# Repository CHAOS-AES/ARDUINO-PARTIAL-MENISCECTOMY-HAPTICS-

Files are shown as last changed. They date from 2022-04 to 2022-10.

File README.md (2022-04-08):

# PARTIAL MENISCECTOMY HAPTICS

This is a repository for a project on reality-based modelling of partial meniscectomy.

This project builds on other open-source projects:
- Arduino SimpleFOC library for BLDC control, MIT Licence (Copyright (c) Antun Skuric).
- Basic Linear Algebra library for Arduino, MIT Licence (Copyright (c) tomstewart89).

Repository contains code and CAD models for:
1) Prototype for collecting force-position data from Acufect Upbiter Punch, with ARDUINO MKR Zero based FSR-sensor and potentiometer.
2) Protype for rendering haptic feedback of partial meniscectomy using self-designed hardware, Arduino DUE with SimpleFOC shield, BLDC motor, and AMT 102V encoder.
3) Arduino code for sensor fusion of real-time finite element simulation and empirical data using Kalman Filter.
4) Visualization of partial meniscectomy punch using Processing.

Prototype for collecting data:


Prototype for haptic rendering:




Instructions for running haptic rendering:
1) Build hardware according to bill-of-materials and CAD-models.
2) Download Arduino code.
3) Install hapticFEM-library, simpleFOC-library, Basic Linear Algebra library.
4) Run Arduino sketch: KF_HapticEstimate_with_FEMlib.ino
5) Launch "Processing" and run "PUNCHER_3D_RevF.pde".

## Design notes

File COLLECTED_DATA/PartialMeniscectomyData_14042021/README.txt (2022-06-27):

This folder contains experimental data from a tool-tissue interaction data collection experiment using an Acufex Upbiter Punch. The data was collected from a cadaveric meniscus.

Folders:
PART I: Samples with tape covering FSR sensor. Idea was to get better force distribution over FSR, but ended up biasing measures (force not being zero unloaded).
PART II: Tape was removed. Zero force on zero load, but pay attention to force behavior.

The dataset consists of five columns:
1) fsrReading - this is the raw reading of the force sensitive resistor.
2) fsrForce - this is the fsr-force converted to Newtons from a calibration function.
3) potVal - this is the raw potentiometer reading.
3) anglePres - this is the potentiometer reading converted to degrees.
4) currentMillis - this is the time stamp in milliseconds.

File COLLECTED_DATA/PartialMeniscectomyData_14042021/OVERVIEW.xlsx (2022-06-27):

 | Tissue Cutting test 14042021
 | Each test includes a series of at least 10 cuts.
Test # | Tests performed | Comments | Time stamp
1 | Blank Slow | Blank cut in sheet of print paper. Tape mounted over FSR to distribute pressure. | 1758
2 | Blank Fast | Blank cut in sheet of print paper. Tape mounted over FSR to distribute pressure. | 1759
3 | Meniscus Slow | Slow and controlled cut in meniscus. Tape mounted over FSR to distribute pressure. | 1804
4 | Meniscus Slow | Slow and controlled cut in meniscus. Tape mounted over FSR to distribute pressure. | 1811
5 | Meniscus Fast | Faster meniscus cut. Tape mounted over FSR to distribute pressure. | 1807
6 | Meniscus Fast | Faster meniscus cut. Tape mounted over FSR to distribute pressure. | 1814
7 | Blank Slow | Blank cut in sheet of print paper. Tape removed. | 1819
8 | Blank Fast | Blank cut in sheet of print paper. Tape removed. | 1821
9 | Meniscus Slow | Slow and controlled cut in meniscus. Tape removed. | 1824
10 | Meniscus Slow | Slow and controlled cut in meniscus. Tape removed. Meniscus removed from knee. | 1839
11 | Meniscus Fast | Faster meniscus cuts. Tape removed. | 1826
12 | Meniscus Fast | Faster meniscus cuts. Tape removed. Meniscus removed from knee. | 1842

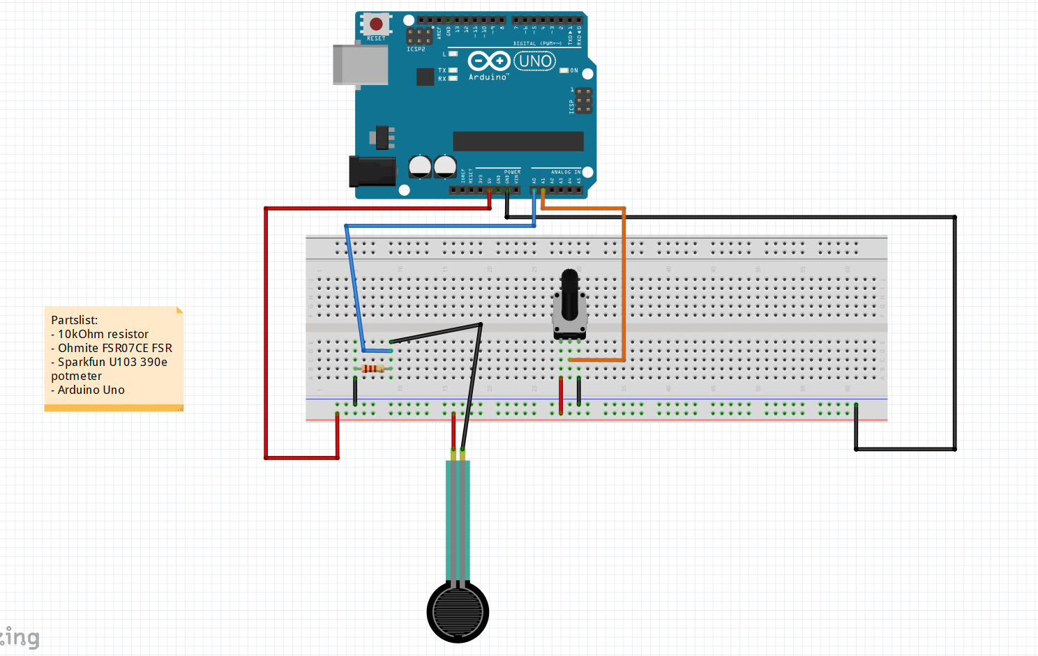
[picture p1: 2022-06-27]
DATA_COLLECTION/schematic.PNG

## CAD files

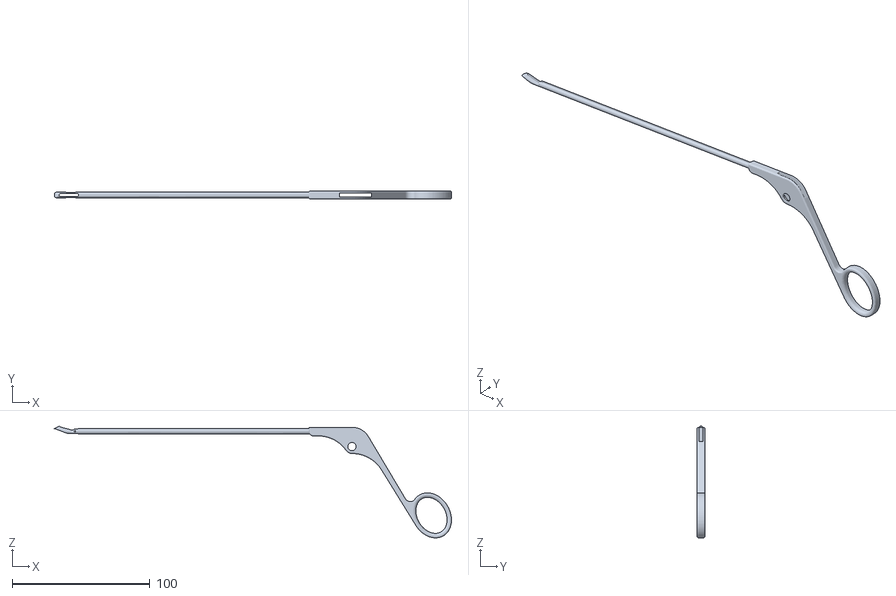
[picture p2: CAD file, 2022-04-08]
HAPTIC_RENDERING/PROCESSING(VISUALIZATION)/PUNCHER_3D_RevF/ACUFEX_PUNCH_MAIN_BODY.obj
287.8 x 5.74 x 81.0

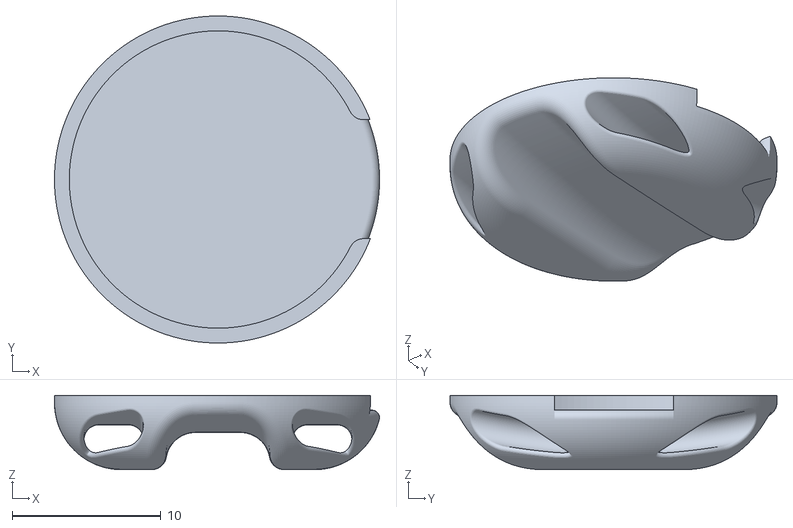
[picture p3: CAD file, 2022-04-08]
DATA_COLLECTION/CAD/3D-print/FSR07_thumb_adapter_RevB.stl
21.9 x 22.0 x 5.00

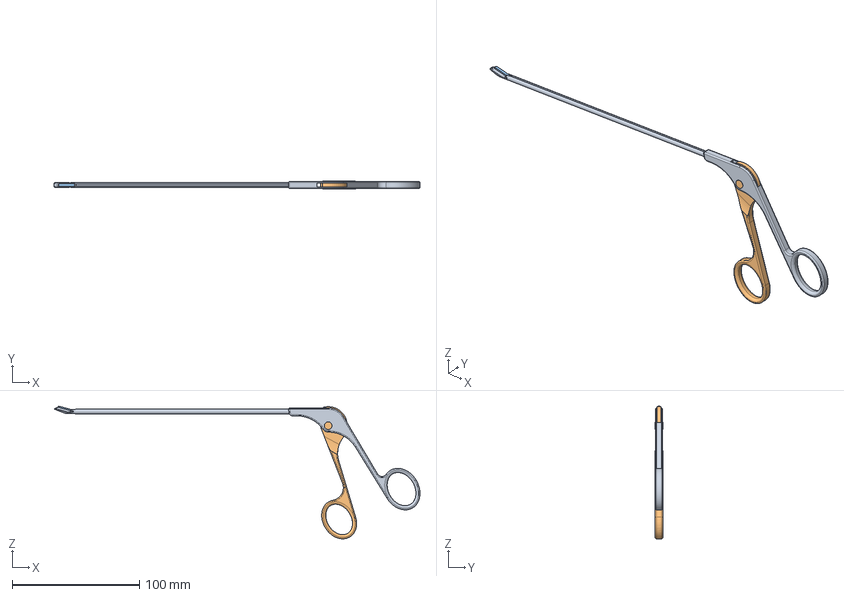
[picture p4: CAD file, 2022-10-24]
DATA_COLLECTION/CAD/STP/ACUFEX_1_5mm_UPBITER_PUNCH_7207735.stp
287.8 x 6.00 x 104.4 mm
ACUFEX_PUNCH_MAIN_BODY
trigger_CSYS_translate
ACUFEX_PUNCHER

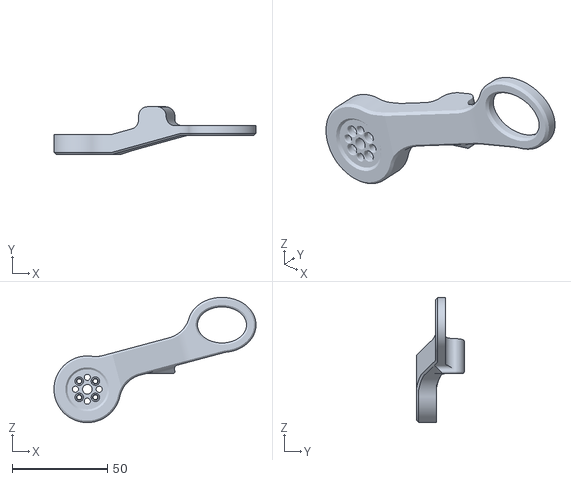
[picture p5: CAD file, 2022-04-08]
HAPTIC_RENDERING/CAD/3D-PRINT/FINGER_HANDLE_REVD.stl
106.1 x 25.0 x 65.7

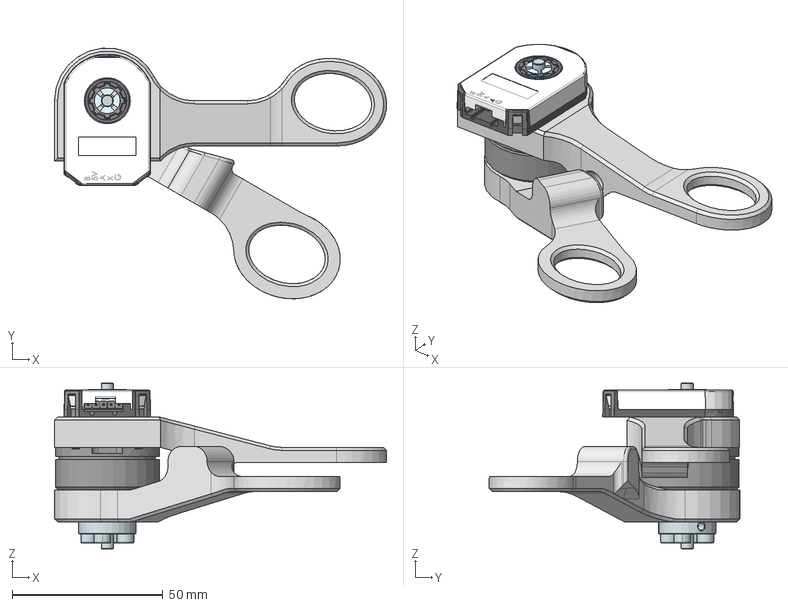
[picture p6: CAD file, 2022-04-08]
HAPTIC_RENDERING/CAD/STEP/FINGER_HAPTIC_DEVICE_REVD.stp
110.1 x 83.1 x 55.0 mm
GM2804_BLDC_motor
THUMB_HANDLE_REVD
FINGER_HANDLE_REVD
Transmitter-board AMT10_AMT-102__id6_x_t
Transmitter-board AMT10_AMT-102__id11_x_t
Transmitter-board AMT10_AMT-102__id16_x_t
Transmitter-board AMT10_AMT-102__id21_x_t
Transmitter-board AMT10_AMT-102__id26_x_t
Transmitter-board AMT10_AMT-102__id31_x_t
Transmitter-board AMT10_AMT-102__id36_x_t
Rotor-board-REV F_id41_x_t
Receiver-board_id46_x_t
AMT10X-Shaft-Adaptor-REV-E_id51_x_t
AMT-Hub-Bottom-REV-B_id56_x_t
AMT-Hub-Top-REV-D1_id61_x_t
AMT-Sleeve-REV-D_ 2 mm__id66_x_t
AMT-102-Top-Cover-REV-I_id71_x_t
AMT-102-Base-REV-K_id76_x_t
4mm_SHAFT
POLULU_4MM_SHAFT_CLAMP
BALL_BEARING_RS_612-5789
BOLT_DIN912_M2X10 x 4
BOLT_DIN912_M2_5X10 x 4
NUT_DIN934_M3 x 6
BOLT_DIN912_M3X12_ x 6
SET_SCREW_M3X6

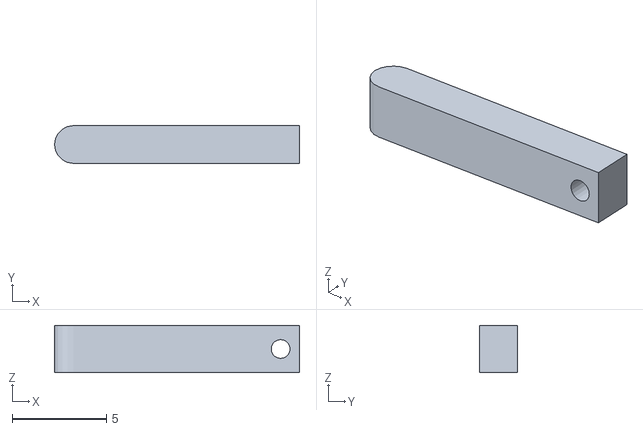
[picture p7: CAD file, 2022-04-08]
HAPTIC_RENDERING/PROCESSING(VISUALIZATION)/PUNCHER_3D_RevF/ACUFEX_PUNCHER.obj
13.0 x 2.00 x 2.50

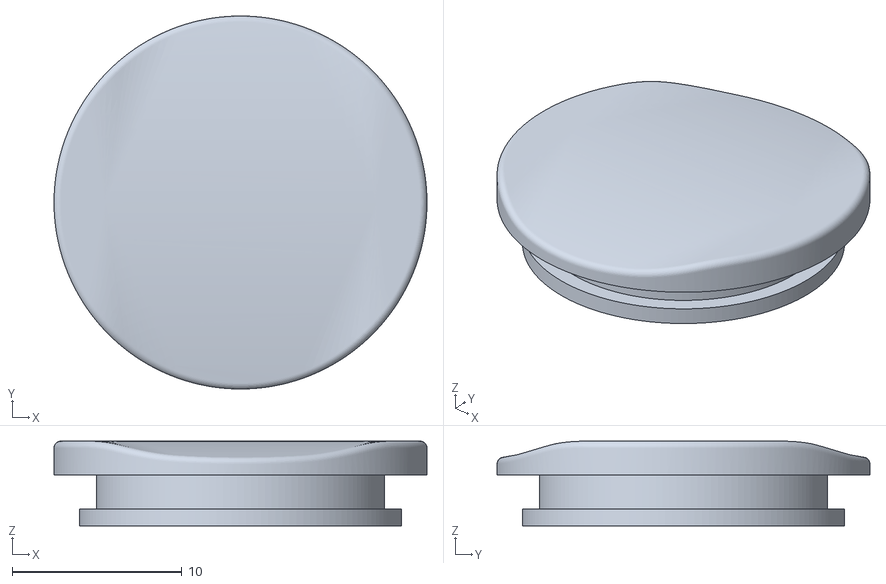
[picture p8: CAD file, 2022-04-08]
DATA_COLLECTION/CAD/3D-print/FSR_TOP.stl
22.0 x 22.0 x 5.00

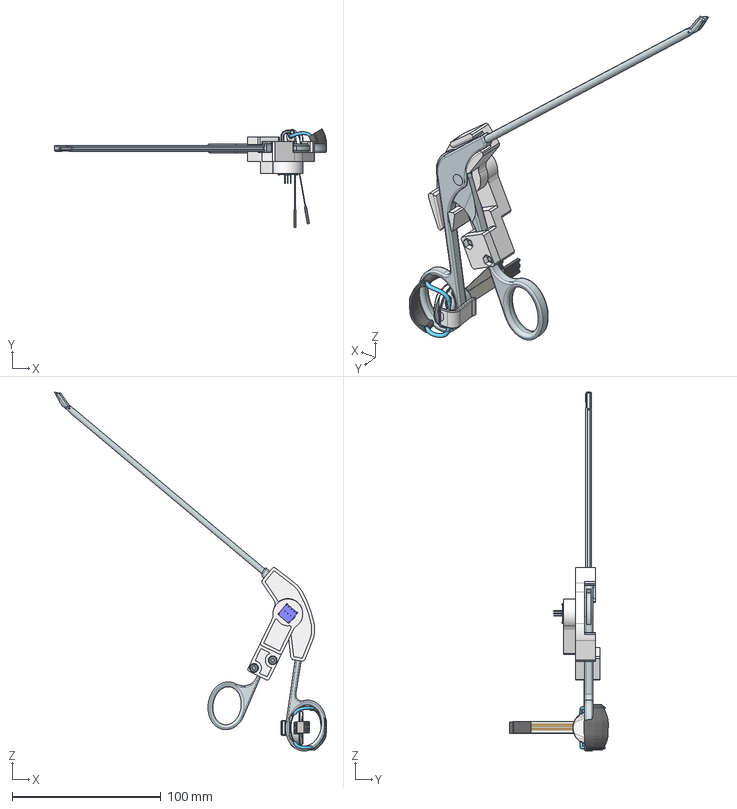
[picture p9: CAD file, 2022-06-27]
DATA_COLLECTION/CAD/STP/Acufex_Puncher_Setup.stp
182.8 x 66.2 x 240.9 mm
FSR07CE x 2
FSR07_thumb_adapter
FSR07_THUMB_ADAPTER_TOP
Rope_attachment
Strap
hand_import
ACUFEX_PUNCH_MAIN_BODY
trigger_CSYS_translate
ACUFEX_PUNCHER
COM-09806_Potentiometer x 2
POTMETER_FRAME_1
POTMETER_FRAME_2
bolt_din912_m3x12 x 2
POTMETER_FRAME_3
FSR_BASE
FSR_TOP

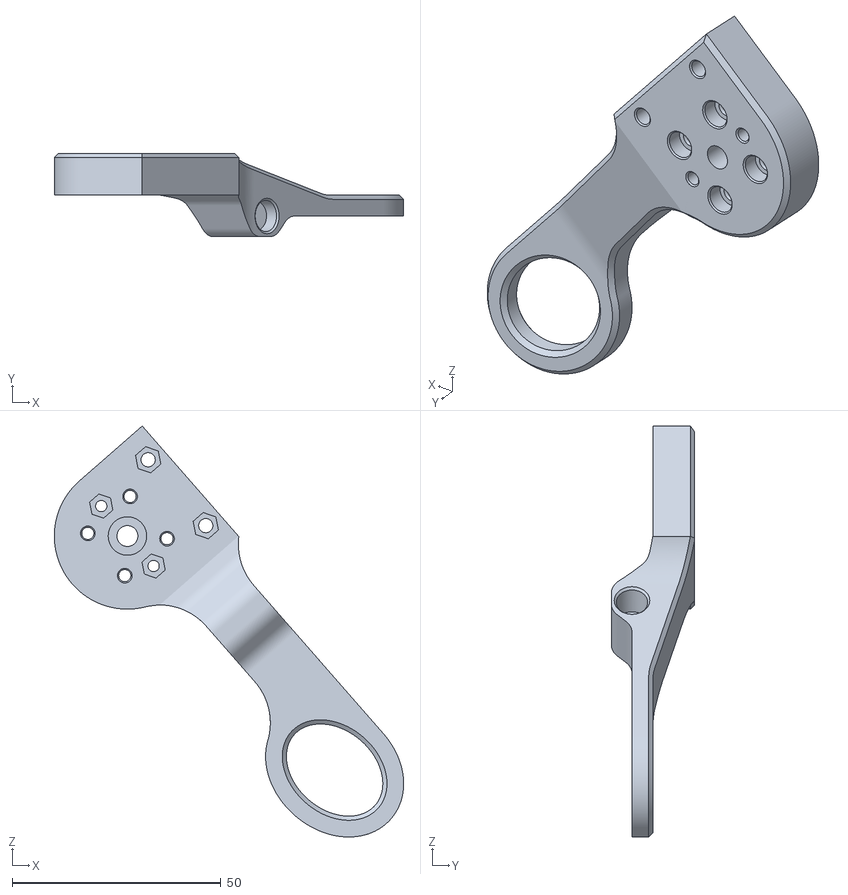
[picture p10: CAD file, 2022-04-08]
HAPTIC_RENDERING/CAD/3D-PRINT/THUMB_HANDLE_REVD.stl
83.6 x 19.9 x 98.4

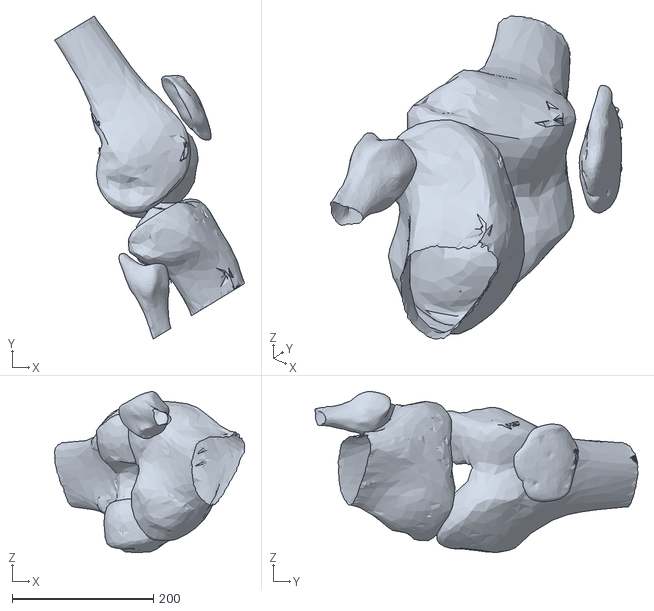
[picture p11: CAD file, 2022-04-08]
HAPTIC_RENDERING/PROCESSING(VISUALIZATION)/PUNCHER_3D_RevF/bone_medullar.obj
269.1 x 457.2 x 228.0

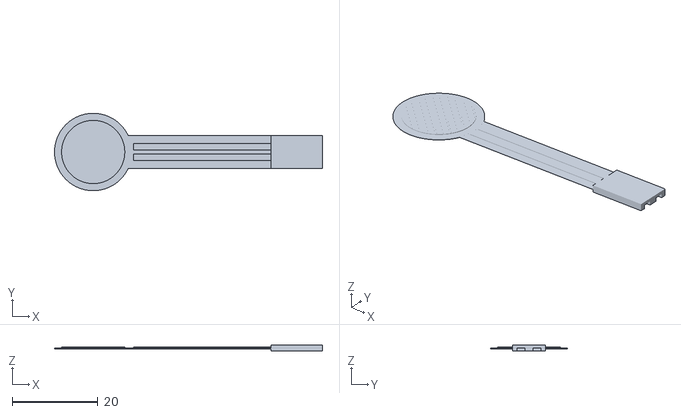
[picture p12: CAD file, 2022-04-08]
DATA_COLLECTION/CAD/3D-print/FSR07CE.stl
62.3 x 18.0 x 1.50

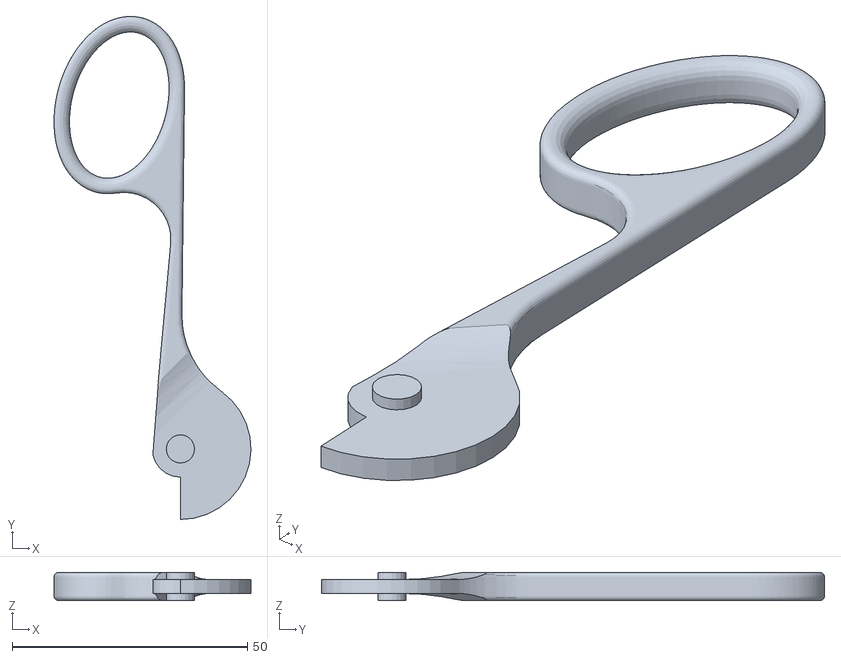
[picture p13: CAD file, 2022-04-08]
HAPTIC_RENDERING/PROCESSING(VISUALIZATION)/PUNCHER_3D_RevF/TRIGGER_NEW_CSYS.obj
41.9 x 106.9 x 6.00

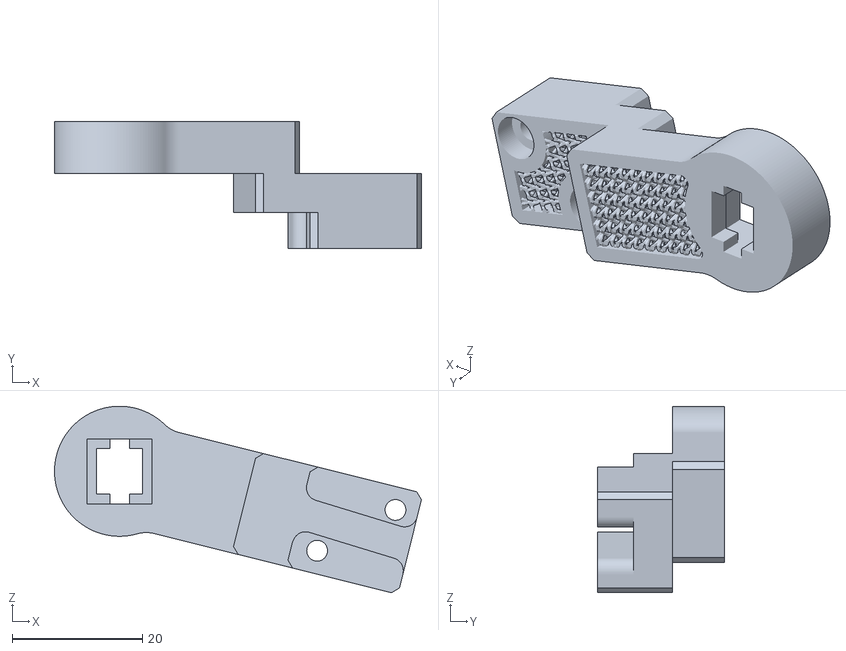
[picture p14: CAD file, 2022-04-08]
DATA_COLLECTION/CAD/3D-print/POTMETER_FRAME_2_RevC.stl
56.4 x 19.5 x 28.7

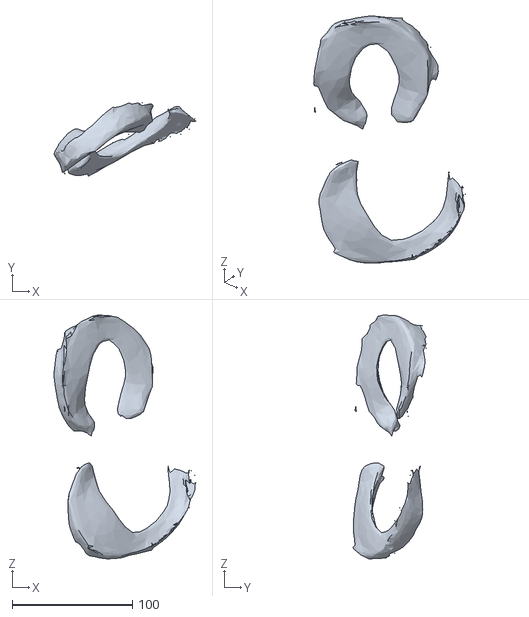
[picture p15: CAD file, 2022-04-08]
HAPTIC_RENDERING/PROCESSING(VISUALIZATION)/PUNCHER_3D_RevF/meniscus.obj
118.1 x 61.4 x 203.2

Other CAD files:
DATA_COLLECTION/CAD/3D-print/FSR_BASE_RevA.stl
HAPTIC_RENDERING/PROCESSING(VISUALIZATION)/PUNCHER_3D_RevF/ACUFEX_TRIGGER.obj
DATA_COLLECTION/CAD/3D-print/FSR07_THUMB_ADAPTER_TOP_RevB.stl
HAPTIC_RENDERING/PROCESSING(VISUALIZATION)/PUNCHER_3D_RevF/fibula.obj
DATA_COLLECTION/CAD/3D-print/POTMETER_FRAME_1_RevC.stl
DATA_COLLECTION/CAD/3D-print/POTMETER_FRAME_3.stl
HAPTIC_RENDERING/PROCESSING(VISUALIZATION)/PUNCHER_3D_RevF/MENISCUS_BUCKET_HANDLE.obj
HAPTIC_RENDERING/PROCESSING(VISUALIZATION)/PUNCHER_3D_RevF/PUNCHER_OBJ.obj
HAPTIC_RENDERING/PROCESSING(VISUALIZATION)/PUNCHER_3D_RevF/tibia.obj

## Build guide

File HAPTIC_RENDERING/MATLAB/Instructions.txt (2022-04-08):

Matlab script for tuning kalman filter parameters Q and R.

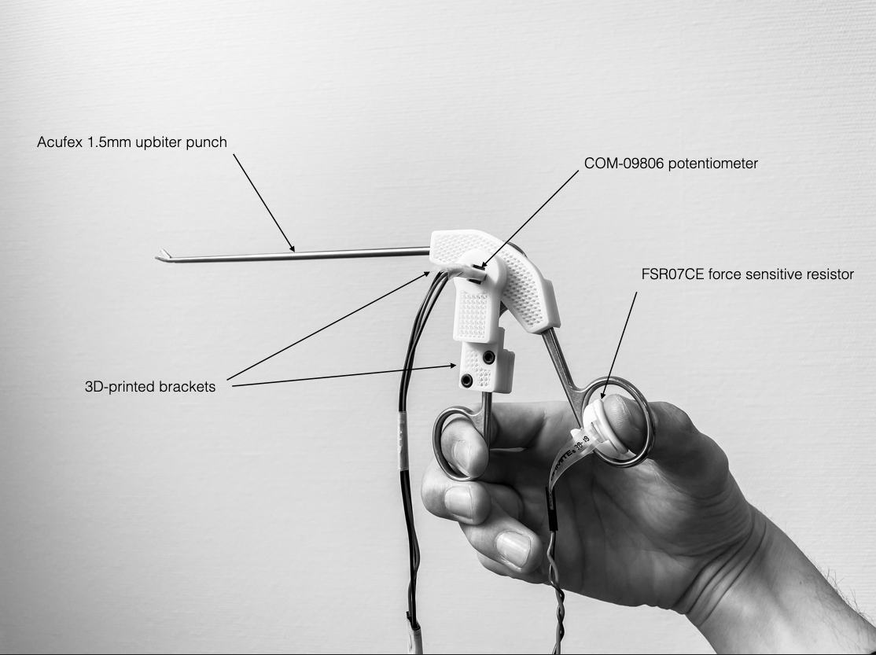
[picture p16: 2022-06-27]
DATA_COLLECTION/setup.PNG

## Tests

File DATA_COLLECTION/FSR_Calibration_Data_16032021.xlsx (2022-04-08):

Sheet: Curve Fitting
FSR Reading | Weight reading (g)
0 | 0 |  | Acceptable readings from 200g to 900g
170 | 60
260 | 250
410 | 300
600 | 350
700 | 400
760 | 450
710 | 500
0 | 0
150 | 130
200 | 200
300 | 250
420 | 300
530 | 400
650 | 500
770 | 600
950 | 700
970 | 800
960 | 900
900 | 1000
1000 | 1100
1023 | 1200
0 | 0
300 | 100
200 | 150
250 | 200
500 | 300
550 | 400
600 | 500
650 | 600
870 | 700
880 | 800
950 | 900
890 | 1000
980 | 1100
950 | 1200
900 | 1300 | Weigh reading (g) | FSR1 | FSR2 | FSR3
 |  | 130 | 150 | 200 | 150
 |  | 200 | 200 | 250 | 200
 |  | 300 | 420 | 500 | 500
0 | 0 | 400 | 530 | 550 | 590
150 | 110 | 500 | 650 | 600 | 670
200 | 200 | 600 | 770 | 650 | 800
500 | 300 | 700 | 950 | 870 | 750
590 | 400 | 800 | 970 | 880 | 850
670 | 500 | 900 | 960 | 950 | 1000
800 | 600
750 | 700
850 | 800
1000 | 900
930 | 1000
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

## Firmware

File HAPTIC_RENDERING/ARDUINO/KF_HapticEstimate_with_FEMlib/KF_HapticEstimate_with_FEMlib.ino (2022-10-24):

/**

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
 
 PROJECT DESCRIPTION: Real time finite-element based haptic rendering with Kalman Filter estimation of force from empirical data. Interfacing with ARDUINO DUE microcontroller, BGM2804 BLDC Motor, CUI AMT 102V Encoder.
 Based on SimpleFOC library for BLDC control (Copyright (c) 2020 Antun Skuric) 
 Finite Element implementation based on MATLAB code by Morten D. Pedersen, NTNU

  */
  
//*************************************************************************************
//DECLARE DEPENDENCIES START***********************************************************
 
#include <SimpleFOC.h> // FOR CONTROLLING BLDC Motor: https://github.com/simplefoc/Arduino-FOC
#include <hapticFEM.hpp>
#include <BasicLinearAlgebra.h> // FOR MATRIX OPERATIONS: https://github.com/tomstewart89/BasicLinearAlgebra 
#include <ElementStorage.h> // For BLA library

//using namespace BLA; //Using namespace basic linear algebra

//DECLARE DEPENDENCIES END************************************************************
//*************************************************************************************


//*************************************************************************************
//INITIALIZATION START*****************************************************************

  #define DOF 5 // Defines number of elements in rubber band model
  

  //Define Kalman Filter matrices
  BLA::Matrix<2,2> Q = {7.0275, 0.02772, 0.2772, 6.1024}; //System covariance matrix
  BLA::Matrix<1> R_FEM = {0.001}; // Measurement variance from FEM
  BLA::Matrix<1> R_empirical = {7.742}; // Measurement variance from empirical measurements
  //BLA::Matrix<1> R_empirical = {0.7742}; // Measurement variance from empirical measurements
  //BLA::Matrix<1> R_empirical = {77.42}; // Measurement variance from empirical measurements
  BLA::Matrix<1> R = R_FEM;

  BLA::Matrix<2,2> A = {1, 1, 0, 1}; //System matrix
  BLA::Matrix<2,2> Ad = A;
  BLA::Matrix<2,1> B = {1, 0};       //Input matrix
  BLA::Matrix<2,1> Bd = B;
  BLA::Matrix<1,2> H = {1, 0};       //Measurement matrix
  BLA::Matrix<2,1> HTransposed = ~H; //Measurement matrix transposed
  BLA::Matrix<1> u = {0};            //Input     
  BLA::Matrix<2,2> Id = {1, 0, 0, 1};//Identity matrix  

  BLA::Matrix<1> forceMeasurement = {0};
  double FEMforceMeasurement = 0;
  float maxFemForce = 0;
  float yieldForce = 7; // [N] Max FEM yield force
  float dTheta = 0;
  float xhDegPreviousStep = 0;
  float forceMovingAvg = 0;
  float forceMovingAvgLast = 0;
  float forceMovingAvgLastLast = 0;
  BLA::Matrix<2,2> Pplus = {0, 0, 0, 0};
  BLA::Matrix<2,1> xhat = {0, 0}; // Initial conditions. Zero force, zero stiffness.
  
  


//*************************************************************************************
//FUNCTION PERFORMING EMPIRICAL FORCE CALCULATION START********************************

BLA::Matrix<1> empiricalData(float xhDeg){
  //This function takes in a position value [deg] and returns a force signal [N]

  //BLA::Matrix<1> empForceMeasurement;
  double empForceMeasurement;
  double theta = (xhDeg - 16)/2; //Offset and scaling of theta range to fit FEM. Remove if not needed.
  
  // <row, column>
  BLA::Matrix<76,1> empForce;
  empForce = {0.000,0.000,0.000,0.008,0.008,0.000,0.000,0.000,0.000,0.008,0.008,0.008,0.008,0.008,0.008,0.008,0.000,0.084,0.228,0.823,1.006,1.789,2.217,2.791,3.313,3.798,4.096,4.187,4.220,4.302,4.344,4.220,4.327,4.236,4.369,4.253,4.277,4.277,4.145,4.072,3.894,3.894,3.999,4.154,3.966,4.015,3.798,3.726,3.750,3.774,3.814,3.679,3.806,3.894,3.950,4.056,4.039,3.983,4.007,3.910,3.894,3.886,4.015,4.031,3.958,3.950,4.031,4.007,4.064,4.015,4.113,4.031,3.983,4.056,4.080,4.344};
  
  BLA::Matrix<76,1> empTheta;
  empTheta = {2.079,2.188,2.300,2.414,2.526,2.636,2.742,2.842,2.939,3.033,3.127,3.222,3.322,3.430,3.547,3.675,3.813,3.961,4.118,4.283,4.453,4.629,4.807,4.988,5.171,5.357,5.545,5.737,5.932,6.132,6.335,6.542,6.752,6.966,7.183,7.404,7.627,7.854,8.083,8.315,8.546,8.777,9.003,9.221,9.429,9.621,9.796,9.950,10.082,10.192,10.280,10.349,10.400,10.438,10.465,10.485,10.500,10.514,10.528,10.543,10.559,10.576,10.595,10.615,10.635,10.656,10.675,10.694,10.712,10.729,10.745,10.761,10.776,10.791,10.806,10.820};

  // Linear interpolation

  for (int i = 0; i<75; i++){
      if ((theta > empTheta(i)) && (theta <= empTheta(i+1))){
          empForceMeasurement = empForce(i) + ((empForce(i+1) - empForce(i))*((theta - empTheta(i))/(empTheta(i+1) - empTheta(i))));
      } 
  }

    if (empForceMeasurement > 4.29){
    empForceMeasurement = 4.29;
  } else if (empForceMeasurement < 0.01){
    empForceMeasurement = 0.01;
  }
  
  return empForceMeasurement;

}

//FUNCTION PERFORMING EMPIRICAL FORCE CALCULATION END**********************************
//*************************************************************************************



//*************************************************************************************
//DECLARE MOTOR AND ENCODER START******************************************************

// BLDC motor & driver instance
BLDCMotor motor = BLDCMotor(7);
BLDCDriver3PWM driver = BLDCDriver3PWM(9, 5, 6, 8);

// encoder instance
Encoder encoder = Encoder(3, 2, 2048);

// Interrupt routine intialisation
// channel A and B callbacks
void doA(){encoder.handleA();}
void doB(){encoder.handleB();}

float target_voltage = 0; //Voltage set point varable

// instantiate the commander
Commander command = Commander(Serial);
void doTarget(char* cmd) { command.scalar(&target_voltage, cmd); }

double xh = 0;       //Handle position [rad]
double vh = 0;       //Handle velocity [rad/s]

unsigned long currentMillis = 0; // [s]
unsigned long previousMillis = 0; // [s]
unsigned long visualRefreshRate = 30; // [Hz] (=30Hz)

RubberBand<DOF> rubber_band;

//DECLARE MOTOR AND ENCODER END********************************************************
//*************************************************************************************





  
void setup() { 

  //*************************************************************************************
  //Initiate BLDC and Encoder start******************************************************
  
  // initialize encoder sensor hardware
  encoder.init();
  encoder.enableInterrupts(doA, doB); 
  // link the motor to the sensor
  motor.linkSensor(&encoder);

  // driver config
  // power supply voltage [V]
  driver.voltage_power_supply = 12;
  driver.init();
  // link driver
  motor.linkDriver(&driver);

  // aligning voltage
  motor.voltage_sensor_align = 3.3; //12?
  // choose FOC modulation (optional)
  motor.foc_modulation = FOCModulationType::SpaceVectorPWM;

  // set motion control loop to be used
  motor.controller = MotionControlType::torque;

  // use monitoring with serial 
  Serial.begin(115200);
  // comment out if not needed
  motor.useMonitoring(Serial);

  // initialize motor
  motor.init();
  // align sensor and start FOC
  motor.initFOC();

  Serial.println(F("Motor ready."));
  _delay(1000);


  //*************************************************************************************
  //Assemble stiffness matrix from mesh size (N)*****************************************
  
  rubber_band.setup();

  //*************************************************************************************
  //Start moving average calculation*****************************************************
  
}

  

void loop() {

  //*************************************************************************************
  //Run FOC loop and get position data*************************************************** 
  motor.loopFOC();

  xh = encoder.getAngle();
  float xhDeg = (xh/M_PI)*180;
  vh = encoder.getVelocity();
  

  //*************************************************************************************
  //CALCULATE FEM-FORCE AND DEFORMED SHAPE FROM TOOL POSITION****************************
  
  auto d = rubber_band.loop(xhDeg);

  //Vizualize deformed shape if needed
  //Serial << "deformedShape: " << d.deformedShape << '\n';

  //Use FEM-simulation as force measurement, and clamp signal within range

  if (d.force < 0){
    FEMforceMeasurement = 0;
  }else if ((d.force > yieldForce)){
    FEMforceMeasurement = yieldForce;
  }else {
    FEMforceMeasurement = d.force;
  }

  //*************************************************************************************
  //KALMAN FILTER HAPTIC FORCE ESTIMATION************************************************

  //STEP 0: Position stepping
  dTheta = xhDeg - xhDegPreviousStep;
  xhDegPreviousStep = xhDeg;
  
  Ad(0,1) = dTheta;
  Bd = B; 

  //STEP 1: Use FEM-simulation as force measurement, and assign uncertainty

  forceMeasurement(0) = FEMforceMeasurement;  //Take measurement
  R = R_FEM;      //Assign measurement uncertainty

  //STEP 2: Estimate haptic force from FEM
  //Predict
  xhat = Ad*xhat + B*u; // A priori force estimate
  BLA::Matrix<2,2> AdTransposed = ~Ad;   // Transpose Ad
  BLA::Matrix<2,2> Pmin = Ad*Pplus*AdTransposed + Q; // A priori covariance matrix

  //Correct
  BLA::Matrix<1> HPHR = H*Pmin*HTransposed + R;   //Calulate (H*Pmin*HTransposed + R)
  BLA::Matrix<1> HPHR_Inverse = HPHR;             //Prepare for taking inverse of HPHR
  Invert(HPHR_Inverse);                           //Take inverse of HPHR (COULD BE PROBLEMS BECAUSE MATRIX IS NOT SQUARE)
  BLA::Matrix<2,1> K = Pmin*HTransposed*HPHR_Inverse; //Compute Kalman Gain
  xhat = xhat + K*(forceMeasurement - H*xhat);  // A posteriori force estimate
  Pplus = (Id - K*H)*Pmin; // A posteriori covariance matrix
  
  //STEP 3: Use empirical data as force measurement
  BLA::Matrix<1> empForceMeasurement = empiricalData(xhDeg);  //Take measurement
  forceMeasurement(0) = empForceMeasurement(0);
  R = R_empirical;  //Assign measurement uncertainty

  //STEP 4: Estimate haptic force from empirical data
   //Predict
  xhat = Ad*xhat + B*u; // A priori force estimate
  AdTransposed = ~Ad;   // Transpose Ad
  Pmin = Ad*Pplus*AdTransposed + Q; // A priori covariance matrix

  //Correct
  HPHR = H*Pmin*HTransposed + R;   //Calulate (H*Pmin*HTransposed + R)
  HPHR_Inverse = HPHR;             //Prepare for taking inverse of HPHR
  Invert(HPHR_Inverse);                           //Take inverse of HPHR (COULD BE PROBLEMS BECAUSE MATRIX IS NOT SQUARE)

  K = Pmin*HTransposed*HPHR_Inverse; //Compute Kalman Gain
  xhat = xhat + K*(forceMeasurement - H*xhat);  // A posteriori force estimate
  Pplus = (Id - K*H)*Pmin; // A posteriori covariance matrix

  float forceEstimate = xhat(0);

  //Moving average filtering
  forceMovingAvg = (forceMovingAvg + forceMovingAvgLast + forceMovingAvgLastLast)/3;
  forceMovingAvgLast = forceMovingAvgLastLast;
  forceMovingAvgLastLast = forceEstimate;


  //*************************************************************************************
  //CONVERT FORCE SIGNAL TO MOTOR CONTROL SIGNAL (VOLTAGE)*******************************

  // Mapping force to voltage
  //double target_voltage = -d.force*1.5; //CASE 1: Uncomment to use only FEM-signal for haptic signal
  //double target_voltage = -empForceMeasurement(0)*2.7; // CASE 2: Uncomment to use only Empirical signal.
  double target_voltage = -forceMovingAvg*2.25; //CASE 3: Uncomment to use kalman filter estimation for haptic signal

  // Cap signal to prevent overloading the motor
  if(target_voltage < -12){
      target_voltage = -12;
  } else if (target_voltage > 0){
    target_voltage = 0;
  }

  // Send signal to motor
  motor.move(target_voltage);


  //*************************************************************************************
  //SEND MESH TO SERIAL MONITOR FOR VISUALIZATION****************************************

  //Serial << deformedShape << '\n'; // Printing deformed shape matrix to serial monitor
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

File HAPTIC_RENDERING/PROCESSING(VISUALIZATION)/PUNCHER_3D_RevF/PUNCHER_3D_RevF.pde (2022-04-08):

// PUNCHER VISUALIZATION
// By Øystein Bjelland, CPS-Lab, NTNU
// Changelog Rev F: Trying to implement camera 3D-orient from this example (https://discourse.processing.org/t/camera-rotation-in-3d-using-mouse/20563) 

import processing.serial.*;
import processing.opengl.*;

Serial myPort; // Create object from Serial class

//General
PShape NTNU;

//3D-view setup
float triggerAngle = 0;
public float angleChange = 0;
float previousTriggerAngle = triggerAngle;
  
PShape mainBody;
PShape trigger;
PShape puncher;
    
PShape meniscus;
PShape bone;
PShape fibula;


//*****************************

//Rubber Band
int DOF = 10;
String val; //Data received from the serial port


float[] deformedMesh = new float[DOF];
float[] node_x = new float[DOF+1];
float[] staticMesh = new float[DOF];

float x_offset = 0;
float y_offset = 0; // =height/2;

float meniscusThickness = 30;
float nodeDistance = 50;
float toolSize = 18;
float toolYPos;
float toolXPos = 1.5;
int toolXPosIndex;

int startTime;
int time;

float a = 0.5;
float b = 2;

//Anatomy transformation parameters
float scaleAnatomy = 0.08;
float translateAnatomyX = -320;
float translateAnatomyY = -220;
float translateAnatomyZ = -140;
float rotateAnatomyX = 20;
float rotateAnatomyY = -100;
float rotateAnatomyZ = -80;

//******************************

//Camera stuff
int grid = 100;
PVector bpos = new PVector();
float bsize = grid;
float bspeedX, bspeedY, bspeedZ;
boolean input1, input2, input3, input4;
float cameraRotateX;
float cameraRotateY;
float cameraSpeed;
int gridCount = 50;
PVector pos, speed;
float accelMag;



void setup() {
    
    //General
    //size(1200, 800, P3D);
    fullScreen(P3D);
    background(0);
    stroke(255);
    strokeWeight(5);
    
    //Camera stuff
    cameraSpeed = TWO_PI / width;
    cameraRotateY = -PI/6;
    pos = new PVector();
    speed = new PVector();
    accelMag = 2;
    
    String portName = Serial.list()[1];  // Put correct port number here
    myPort = new Serial(this, portName, 115200);  //Put correct baud rate at last entry!
    myPort.bufferUntil('\n');
   
     
    //3D-view stuff
    mainBody = loadShape("ACUFEX_PUNCH_MAIN_BODY.obj");
    trigger = loadShape("TRIGGER_NEW_CSYS.obj");
    puncher = loadShape("PUNCHER_OBJ.obj");
    //meniscus = loadShape("meniscus.obj");
    //bone = loadShape("bone_medullar.obj");
    bone = loadShape("tibia.obj");
    fibula = loadShape("fibula.obj");
    meniscus = loadShape("MENISCUS_BUCKET_HANDLE.obj");
    
    
    shape(mainBody, 80, 0);
    mainBody.rotateX(PI/2);
    mainBody.translate(-23., 49, 0);
    
    shape(trigger, 0, 0);
    trigger.rotateZ(radians(20));
    
    shape(puncher, 0, 0);
    puncher.rotateZ(radians(35));
    puncher.translate(-202,-12,0);
   
    shape(meniscus, 0, 0);
    meniscus.scale(scaleAnatomy);   
    meniscus.rotateY(radians(rotateAnatomyY));   
    meniscus.rotateZ(radians(rotateAnatomyZ));
    meniscus.rotateX(radians(rotateAnatomyX));
    meniscus.translate(translateAnatomyX,translateAnatomyY,translateAnatomyZ);
    meniscus.setFill(color(255,0,0));
     
    shape(bone, 0, 0);
    bone.scale(scaleAnatomy);
    bone.rotateY(radians(rotateAnatomyY));
    bone.rotateZ(radians(rotateAnatomyZ));
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

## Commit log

2022-06-27 Cleaned up folder structure
    [OVERVIEW.xlsx, Tissue_Cutting_Test_1404202.xlsx]
2022-06-27 Added instructions
    [4mm_SHAFT.prt, 5mm_ADAPTER.prt, ACUFEX_1_5mm_UPBITER_PUNCH_7207735.prt, ACUFEX_1_5mm_UPBITER_PUNCH_7207735.stp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]

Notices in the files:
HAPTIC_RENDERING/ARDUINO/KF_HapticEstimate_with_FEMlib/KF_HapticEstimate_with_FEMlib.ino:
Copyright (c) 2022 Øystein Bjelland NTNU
